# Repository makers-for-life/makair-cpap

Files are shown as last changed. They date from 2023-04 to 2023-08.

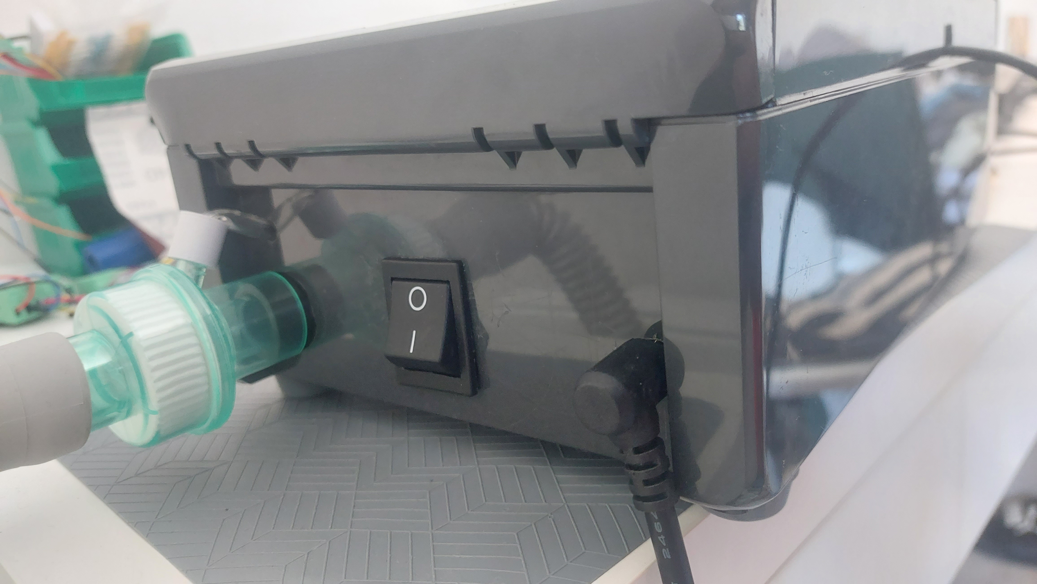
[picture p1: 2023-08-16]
Parts-CPAP/Case_V2/Output.jpg

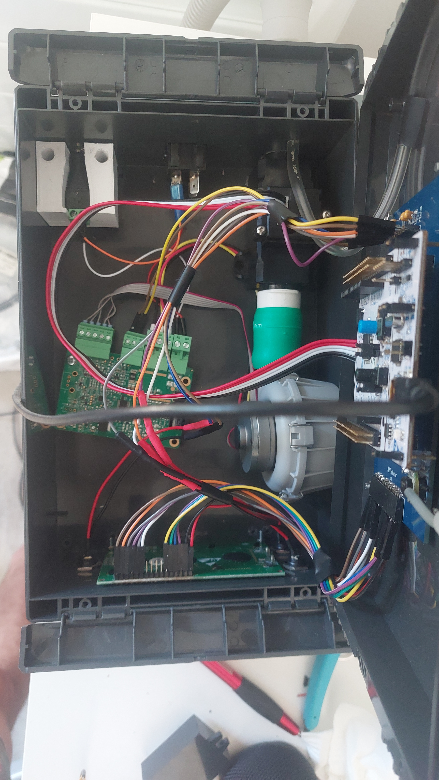
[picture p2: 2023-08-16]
Parts-CPAP/Case_V2/Input.jpg

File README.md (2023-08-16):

# MakAir CPAP

**Continuous Positive Airway Pressure ventilator for sleep apnea. Variant of the MakAir general-purpose ventilator.**

## Conception

This file lists all the documents that concern the design of the CPAP ventilator and the justification of all the choices that have been made on the system

[Conception-CPAP](https://github.com/makers-for-life/makair-cpap/tree/master/Conception-CPAP)

## Educational videos

This file lists the series of instructional videos on the progress of the CPAP ventilator project. You can find all the chapters of the project with educational files

[Educational videos](https://github.com/makers-for-life/makair-cpap/tree/master/Educational-videos)

## Firmware 

This file lists all the programs (Arduino, C++) that has been realized during the project. You can find the main program of the CPAP respirator which integrates the different operating modes

[Firmware-CPAP](https://github.com/makers-for-life/makair-cpap/tree/master/Firmware-CPAP)

## Motherboard 

This file lists all documents concerning the design and production of the PCB (BOM, Gerber, etc.).

[Motherboard-CPAP](https://github.com/makers-for-life/makair-cpap/tree/master/Firmware-CPAP)

## Parts

This file lists all files related to the mechanics of the CPAP ventilator. You can find the different parts in STL file and FreeCAD files

[Parts-CPAP](https://github.com/makers-for-life/makair-cpap/tree/master/Parts-CPAP)

## Various

This file lists various files that relate to specific information about the PPC ventilator

[Various-CPAP](https://github.com/makers-for-life/makair-cpap/tree/master/Various-CPAP)

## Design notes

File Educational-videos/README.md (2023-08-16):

| Chapter  | Content | Video  | File |
| ------------- | ------------- | ------------- | ------------- |
| 0  | **Introduction**  | [Introduction](https://www.youtube.com/watch?v=J2UsDe6RBvU&ab_channel=MakAir-Projetopensource) |  |
| 1  | This chapter will explain how to format a customer's need by structuring it with Sysml diagrams.  | [Chapter 1](https://www.youtube.com/watch?v=lZZDJNnGtbw&ab_channel=MakAir-Projetopensource)  | [Terms of reference](https://github.com/makers-for-life/makair-cpap/tree/master/Conception-CPAP)   |
| 2  | This chapter will explain the MCSE approach and how to use it to define the different I/O and system functions. |[Chapter 2](https://www.youtube.com/watch?v=BaCOPvmWCng&t=80s&ab_channel=MakAir-Projetopensource) | [MCSE](https://github.com/makers-for-life/makair-cpap/tree/master/Conception-CPAP)  |
| 3  | This chapter will explain how to choose the right components for each functional block defined above. Explain some important parameters to consider when choosing components. | [Chapter 3](https://www.youtube.com/watch?v=_1S2HhT8ymI&t=1s&ab_channel=MakAir-Projetopensource) | [Technological Choice](https://github.com/makers-for-life/makair-cpap/tree/master/Conception-CPAP)  |
| 4  | This chapter will explain why it is absolutely necessary to read the component datasheets and how this will allow us to have an electronic base of the system (definition of the pins for each component + realization of the electronic circuits).  | [Chapter 4](https://www.youtube.com/watch?v=aWXtmY03doI&ab_channel=MakAir-Projetopensource) | [Schematic](https://github.com/makers-for-life/makair-cpap/blob/master/Various-CPAP/Circuit_prototypage.png) |
| 5  | This chapter will explain how to define unit tests for each component to validate their operation against the requirements of the specifications.  | [Chapter 5](https://www.youtube.com/watch?v=EbR67JvbmO0&ab_channel=MakAir-Projetopensource) |[Unit tests](https://github.com/makers-for-life/makair-cpap/blob/master/Conception-CPAP/Tests_PPC.pdf)  |
| 6  | This chapter will explain what an IDE is, the different steps between the Arduino code and the binary file for the microcontroller and how to configure a compiler. | [Chapter 6](https://drive.google.com/file/d/1q3lwLBPiozaliIyiF1mZfMr3rwGGGQcm/view?usp=sharing)  | [Tuto STM32duino](https://github.com/makers-for-life/makair-cpap/blob/master/Educational-videos/Educational-sheets/Tuto_stm32duino.pdf)  |
| 7  | This chapter will explain how the blower works, the programming to make it work and the unit tests of the component. | [Chapter 7](https://www.youtube.com/watch?v=EbR67JvbmO0&ab_channel=MakAir-Projetopensource) | [Blower](https://github.com/makers-for-life/makair-cpap/blob/master/Educational-videos/Educational-sheets/Ptech_Blower.pdf)  |
| 8  | This chapter will explain how the flow meter works, the programming to make it work and the unit tests of the component.  |  [Chapter 8](https://drive.google.com/file/d/1uNUySGZBNgJsLLCi5F49UqdtfRMHSRPB/view?usp=sharing) | [Flow meter](https://github.com/makers-for-life/makair-cpap/blob/master/Educational-videos/Educational-sheets/Ptech_debitmetre.pdf)  |
| 9  | This chapter will explain how the pressure sensor works, the programming to make it work and the unit tests of the component. |  [Chapter 8](https://drive.google.com/file/d/1uNUySGZBNgJsLLCi5F49UqdtfRMHSRPB/view?usp=sharing) | [Pressure Sensor](https://github.com/makers-for-life/makair-cpap/blob/master/Educational-videos/Educational-sheets/Ptech_capteur_pression.pdf)  |
| 10  | This chapter will explain how to set up an HMI.  |  [Chapter 9](https://drive.google.com/file/d/1seV6_qKShw0mvWmM2Q1Elv6sRm0VnmUq/view?usp=sharing) | [HMI](https://github.com/makers-for-life/makair-cpap/blob/master/Educational-videos/Educational-sheets/Ptech_IHM.pdf) |
| 11  | This chapter will explain the integration (electronics and software) of each component seen previously to realize the prototype of the PPC ventilator. | [Chapter 10](https://drive.google.com/file/d/1VzoYUgVaH1z69m--aW6JiqTvfR3ldkRQ/view?usp=sharing) | [Integration](https://github.com/makers-for-life/makair-cpap/blob/master/Educational-videos/Educational-sheets/Ptech_Integration.pdf) |
| 12  | This chapter will explain the different parts to model and print in order to have a more presentable and usable prototype during its operation. | [Chapter 11](https://drive.google.com/file/d/1v5jeXeAJxhkbmkdimZctG2w2wa8iBlUA/view?usp=sharing)  | [Parts](https://github.com/makers-for-life/makair-cpap/tree/master/Parts-CPAP) |
| 13  | This chapter will explain how to model each 3D part in FreeCAD.  | [Chapter 11](https://drive.google.com/file/d/1v5jeXeAJxhkbmkdimZctG2w2wa8iBlUA/view?usp=sharing) | [CAD](https://github.com/makers-for-life/makair-cpap/blob/master/Educational-videos/Educational-sheets/Maquette_3D.pdf) |
| 14  | This chapter will explain the parameters to configure when printing the part modeled with Ultimaker Cura. | [Chapter 12](https://drive.google.com/file/d/1JHjJFGdZ1aSK9p1exW7JsYgn3sB551wM/view?usp=sharing) |  [3D printing](https://github.com/makers-for-life/makair-cpap/blob/master/Educational-videos/Educational-sheets/Maquette_3D.pdf) |
| 15  | This chapter will explain how to program a simple PPC mode in order to have a system that meets the specifications. |  [Chapter 13](https://drive.google.com/file/d/1Ri6_7VYuK2wYm5BPET0OP5y3Fja_Plpz/view?usp=sharing) | [Firmware](https://github.com/makers-for-life/makair-cpap/tree/master/Firmware-CPAP) [/ PPC Mode](https://github.com/makers-for-life/makair-cpap/blob/master/Educational-videos/Educational-sheets/Respirateur_PPC.pdf)  |
| 16  | **Conclusion** | [Chapter 14](https://drive.google.com/file/d/1DnsZAroqMhL1uKgiich44XQaq05BFfQ1/view?usp=sharing) |  |

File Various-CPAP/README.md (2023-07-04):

## Caractéristiques 

This document contains all the characteristic curves of the CPAP ventilator

## Nomenclature

This document lists all the components and references that make up the CPAP ventilator

## Circuit Prototypage

This document is a schematic diagram of the system circuit.

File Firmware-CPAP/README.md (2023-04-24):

## Arduino Code

This file contains all the Arduino codes for the prototyping of the system

## Firmware

| Component  | Includes | Sources  | Main |
| ------------- | ------------- | ------------- | ------------- |
| Blower  | [.h](https://github.com/makers-for-life/makair-cpap/blob/master/Firmware-CPAP/Includes/blower.h)  | [.cpp](https://github.com/makers-for-life/makair-cpap/blob/master/Firmware-CPAP/Sources/blower.cpp) | [.ino](https://github.com/makers-for-life/makair-cpap/blob/master/Firmware-CPAP/Main/Blower_fichier.ino) |
| AirFlow meter  | [.h](https://github.com/makers-for-life/makair-cpap/blob/master/Firmware-CPAP/Includes/airflowSensor.h)  | [.cpp](https://github.com/makers-for-life/makair-cpap/blob/master/Firmware-CPAP/Sources/airflowSensor.cpp) | [.ino](https://github.com/makers-for-life/makair-cpap/blob/master/Firmware-CPAP/Main/Debitmetre_fichier.ino) |
| Pressure Sensor  | [.h](https://github.com/makers-for-life/makair-cpap/blob/master/Firmware-CPAP/Includes/pressureSensor.h)  | [.cpp](https://github.com/makers-for-life/makair-cpap/blob/master/Firmware-CPAP/Sources/pressureSensor.cpp) | [.ino](https://github.com/makers-for-life/makair-cpap/blob/master/Firmware-CPAP/Main/Pressure_Sensor_fichier.ino) |
| HMI  | [.h](https://github.com/makers-for-life/makair-cpap/blob/master/Firmware-CPAP/Includes/IHM.h)  | [.cpp](https://github.com/makers-for-life/makair-cpap/blob/master/Firmware-CPAP/Sources/IHM.cpp) | |
| PPC  | [.h](https://github.com/makers-for-life/makair-cpap/blob/master/Firmware-CPAP/Includes/PPC.h)  | [.cpp](https://github.com/makers-for-life/makair-cpap/blob/master/Firmware-CPAP/Sources/PPC.cpp) | [.ino](https://github.com/makers-for-life/makair-cpap/blob/master/Firmware-CPAP/Main/Respirateur_PPC.ino) |

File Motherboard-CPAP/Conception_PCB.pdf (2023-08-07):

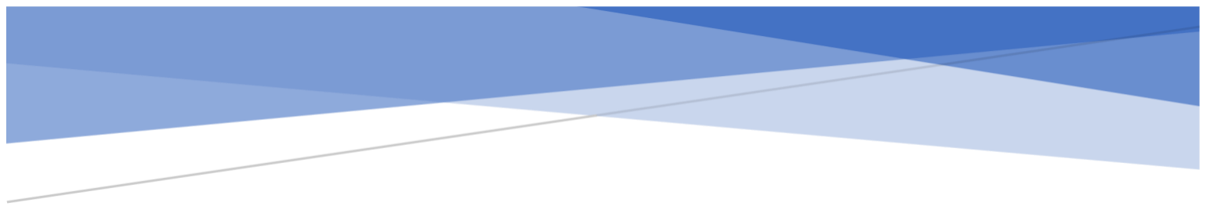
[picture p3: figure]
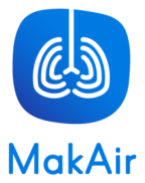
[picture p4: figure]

## BOUTRY Loan

### Alternant sur le projet MakAir

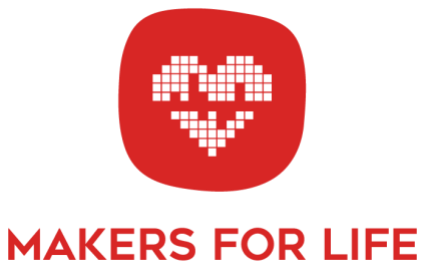
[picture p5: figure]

# PCB du Respirateur PPC

Ce document fait partie d’une série de livrables concernant la conception et le prototypage d’un respirateur à pression positive continue pour diminuer l’apnée du sommeil d’un patient

Ce livrable a pour but d’expliquer le développement du PCB du respirateur PPC afin de rendre le système plus fiable et moins encombrant. Nous pouvons retrouver toutes les solutions et composants choisies à mettre en place sur le PCB.

## Table des matières

Table des figures | 2
Comment concevoir un PCB ? | 3
Réalisation du schéma électronique | 3
Recherche des composants | 4
Routage de la carte | 5
Validation de la carte | 5
Présentation de la carte | 6
Schéma électronique | 6
Routage de la carte | 7
Validation de la carte | 8
Annexe | 10
BOM de la carte | 10

## Table des figures

Figure 1 : Schéma du capteur de pression | 3
Figure 2 : Recherche de composant | 4
Figure 3 : Schématique de la carte | 6
Figure 4 : TopLayer du PCB | 7
Figure 5 : BottomLayer du PCB | 7
Figure 6 : Photos du PCB (non assemblé et assemblé) | 8

## Comment concevoir un PCB ?

La conception d’une carte électronique se fait en 4 étapes :
- Réalisation du schéma électronique
- Recherche des composants
- Routage de la carte
- Validation de la carte.

Nous allons utiliser le logiciel EasyEDA pour concevoir notre carte, c’est un logiciel gratuit de conception de carte développé par JLCPCB (fabricant de PCB).

### Réalisation du schéma électronique

La première étape de la conception d’une carte est la réalisation d’une carte électronique afin de créer la base électronique de votre PCB. C’est dans cette étape qu’on relie les signaux de contrôle et d’alimentation entre le microcontrôleur et les différents composants. On va aussi mettre en place des fonctions électroniques (filtrage, amplification, …), améliorer la protection CEM (comptabilité électromagnétique) ou encore mettre des composants indispensables (capacité de découplage, LDO, …).

Pour imager l’étape, nous allons réaliser le câblage du capteur de pression :

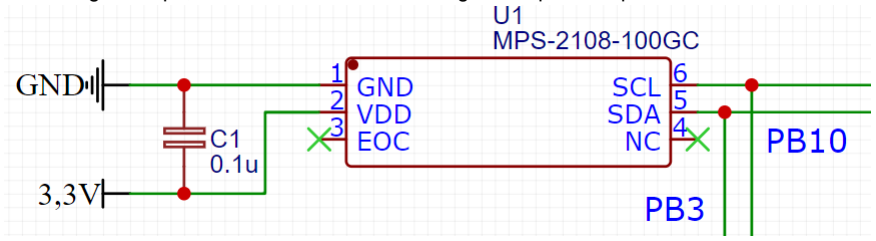
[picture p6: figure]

Figure 1 : Schéma du capteur de pression

Pour les signaux d’alimentation GND et VDD, on place des supply flags comme ci-dessous :

Ensuite on définit le VCC à 3,3V pour correspondre à l’alimentation du microcontrôleur. Pour le signal EOC et NC, on place un « Not Connect Flag » :

Enfin on relie la pin PB10 (broche 14 de U8) à SCL et PB3 (broche 8 de U8) à SDA qui correspondent à des broches de communication I2C du microcontrôleur :

Pour finaliser le câblage du capteur de pression, il faut placer une capacité (0,1µF) de découplage entre VDD et GND et placer des résistances en parallèle des signaux SCL et SDA comme ci-dessous :

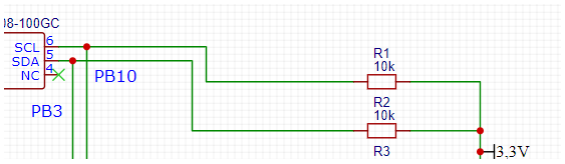
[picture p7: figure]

Le câblage du capteur de pression est réalisé. Il est important d’être rigoureux sur cette étape, on peut utiliser des logiciels comme LTSpice pour simuler le câblage et valider au préalable le schéma électronique.

### Recherche des composants

Cette étape consiste à choisir les composants du schéma électronique. Pour les résistances et condensateurs nous allons choisir entre des composants traversants ou CMS. Pour les connecteurs, nous allons choisir le pas entre chaque trou (pour notre cas, nous allons choisir que des pas de 2,54 mm). Pour le capteur de pression, on va choisir la référence de notre capteur de pression. Cette étape va permettre d’avoir les empreintes de chaque composant pour le routage de la carte. Avec EasyEDA, cette étape est automatiquement faite quand on place les composants sur le schéma mais il peut arriver sur des logiciels (ex : Kicad) qu’on doit rechercher ou créer des empreintes. Pour bien choisir les empreintes des composants sur EasyEDA, on doit aller sur « Library » rechercher la référence du composant (ex : pressure sensor MPS) et le placer sur le schéma :

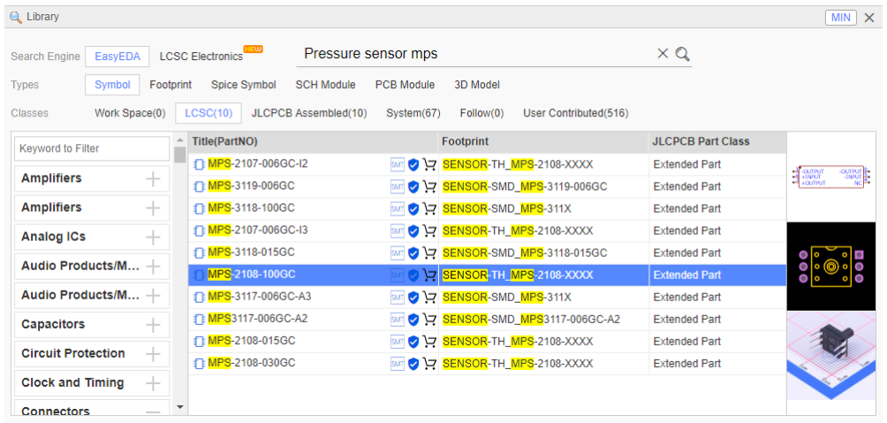
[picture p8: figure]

Figure 2 : Recherche de composant

Dès que on a placé tous les composants, on génére le BOM (Bill of materials) pour récupérer tous les détails des composants sur un tableur. Le BOM de la carte électronique du respirateur PPC est en Annexe.

### Routage de la carte

Cette étape consiste à positionner les composants et relier les signaux avec des pistes. C’est en quelque sorte la construction de la carte. Cela va définir beaucoup de paramètres : le dimensionnement de la carte, le nombre de couches au PCB, la largeur des pistes et le nombre de vias (connexion entre 2 couches). C’est aussi la partie la plus « créative » de la conception puisque on a énormément de possibilités pour router la carte (si on a des contraintes, les possibilités vont forcément diminuer). Au vu du nombre de possibilités pour le routage de la carte, il est important de connaître des règles indispensables :

- La largeur des pistes : Plus la tension parcourant la piste est haute, plus la largeur de votre piste est grande. Dans notre cas, les signaux d’alimentation sont à 1 mm et les signaux de contrôle sont à 0,254 mm.
- Le diamètre des trous/vias (composant traversant) : le diamètre de l’empreinte (zone servant à souder les composants) doit être 2 fois plus grande que le trou
- Aucun angle droit sur les pistes : il est important de ne pas avoir d’angle à 90° sur les pistes afin de les renforcer dans la durée
- La piste doit toujours arriver droite sur l’empreinte :
- Plan de masse : Un plan de masse est une zone reliant toutes les broches GND en commun. Cela permet d’avoir qu’une seule masse en commun pour tous les composants pour éviter des problèmes sur l’alimentation de votre carte. Pour notre cas on la met sur la partie composant (Top) de notre carte :

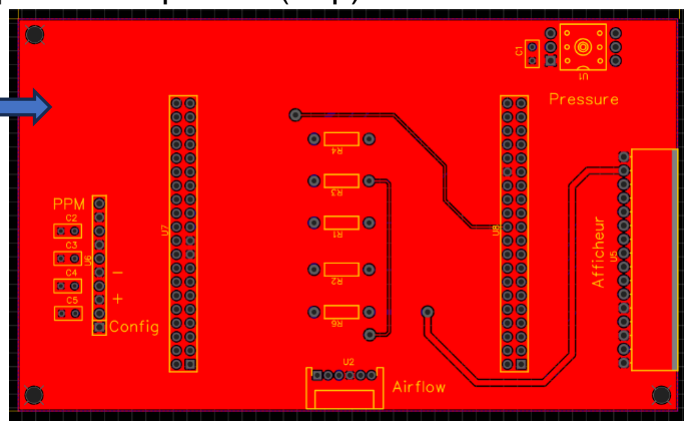
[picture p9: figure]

- Placer des vias si on n’a pas le choix : il est important d’avoir le moins de vias possibles sur votre carte
- Placer la capacité de découplage au plus près du composant :

### Validation de la carte

Cette dernière étape concerne les tests unitaires pour chaque composant afin de valider le fonctionnement de la carte. Pour cette étape il est important d’assembler au fur à mesure la carte pour tester une fonction seule pour retrouver plus facilement le problème s’il y en a un. Dès qu’on a testé unitairement chaque composant, on réalise un test d’intégration pour tester la carte dans sa globalité. Pour avoir une meilleure visibilité sur les tests, on met les résultats de chaque test dans un tableur.

Plan de
masse

## Présentation de la carte

Le but du PCB est de développer une carte permettant d’enlever les fils du prototypage et de placer chaque composant du système sur la carte. Cela va permettre de rendre le système plus fiable et moins encombrant au niveau électronique. Le PCB est une première version de prototypage, c’est pour cela que l’on utilise seulement des connecteurs pour placer les composants (microcontrôleur, débitmètre, capteur de pression et IHM).

### Schéma électronique

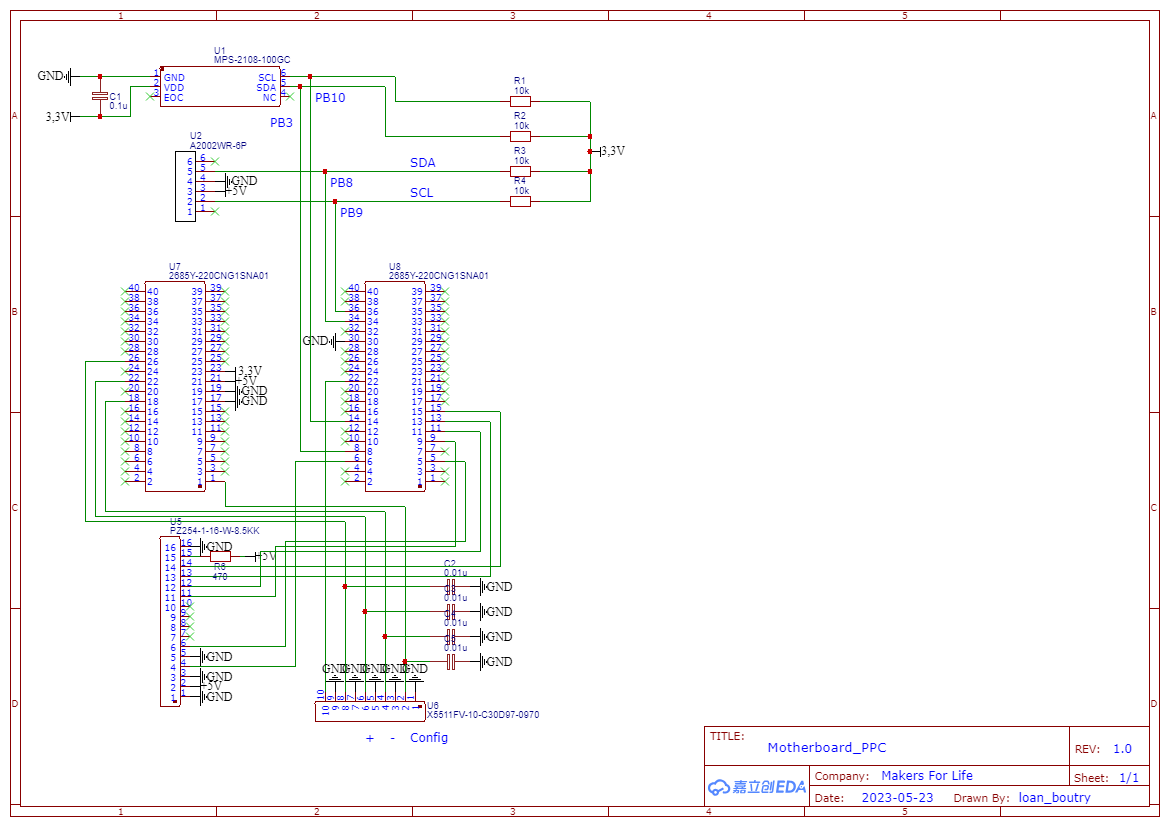
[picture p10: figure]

Figure 3 : Schématique de la carte

Nom | Rôle | Remarques
U1 | Emplacement du capteur de pression | Reference : ABP2MRRT060MD2A3XX
U2 | Connecteur du débitmètre | Reference : Honeywell Zephyr
U5 | Connecteur de l’afficheur LCD (Communication en série) | Reference : Displaytech 204A
U6 | Connecteur des boutons poussoirs | Câblage en Pull-Up
U7/U8 | 2 connecteurs pour la Nucleo STM32F411RE
R1..4 | Résistances 10k pour les 2 communications I2C
R5 | Résistance 470Ω pour la luminosité de l’afficheur
C1 | Capacité de découplage de 0,1µF pour le capteur de pression
C2..C5 | Capacités de 0,01µF pour une protection CEM
H1..H4 | Connecteurs pour les boutons poussoirs de l’IHM | 3 boutons sont utilisés (+, - et config). Un 4ème est ajouté si besoin
H5 | Connecteur du blower pour le signal PPM

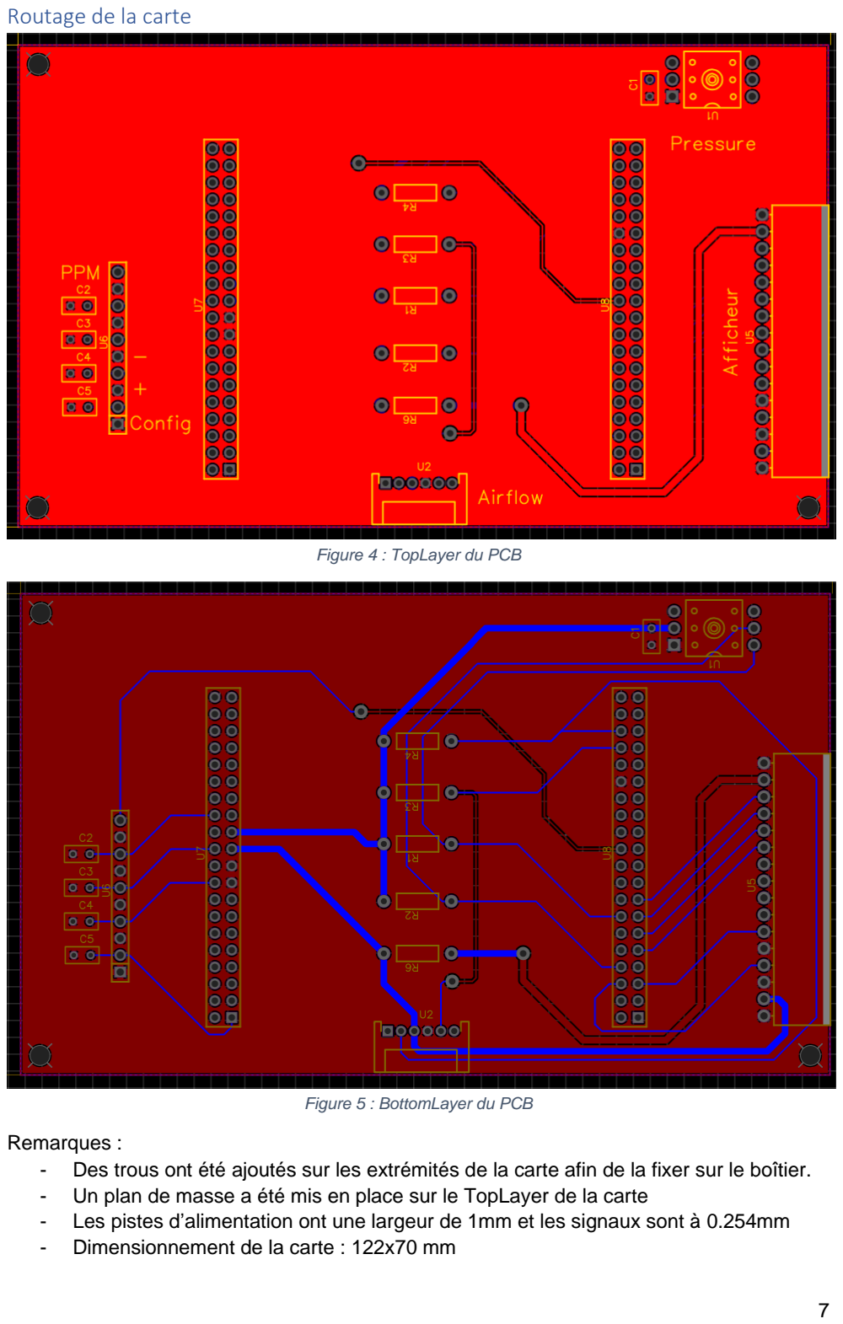
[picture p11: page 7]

### Routage de la carte

Figure 4 : TopLayer du PCB

Figure 5 : BottomLayer du PCB

Remarques :
- Des trous ont été ajoutés sur les extrémités de la carte afin de la fixer sur le boîtier.
- Un plan de masse a été mis en place sur le TopLayer de la carte
- Les pistes d’alimentation ont une largeur de 1mm et les signaux sont à 0.254mm
- Dimensionnement de la carte : 122x70 mm

### Validation de la carte

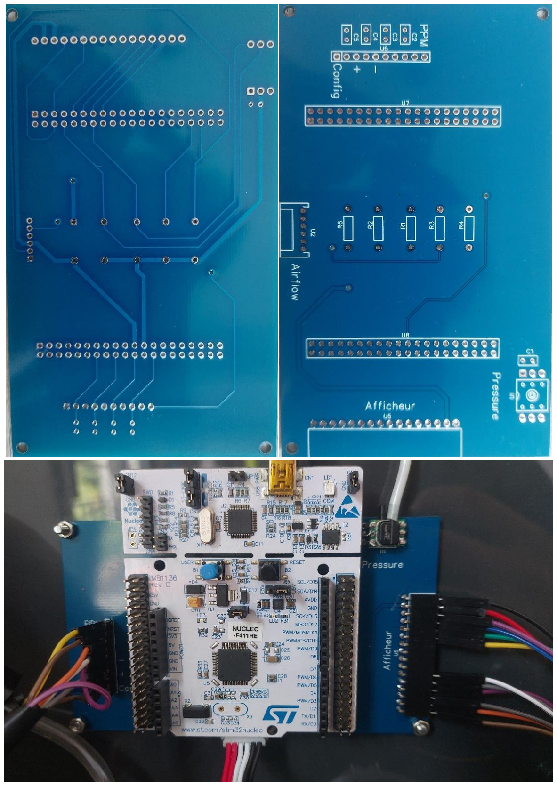
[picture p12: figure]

Figure 6 : Photos du PCB (non assemblé et assemblé)

Nous allons vérifier les alimentations s’il n’y a aucun problème (court-circuit, baisse de tension) et si les signaux de contrôle correspondent au programme intégré dans le microcontrôleur. S’il y a des modifications à réaliser, nous referons une deuxième version de la carte.

V1 :

Elément testé sur le PCB | Validation ? | Remarques
Alimentation | OUI | - Conversion du 24V au 5V est fonctionnel pour le µC - Carte de contrôle alimentée en 24V
Blower | OUI | - Pas besoin de souder le via - Penser à souder le GND du µc au PCB
Débitmètre | OUI | - Faire attention à ne pas confondre le 3,3V et le 5V - Câbler les 5 résistances pour faire fonctionner le capteur
Capteur de pression | NON | - Refaire le positionnement du capteur de pression (validé si l’on change de sens) - Faire attention au sens du capteur lors de la soudure
IHM | NON | - Problème d’alimentation sur la Pin d’alimentation de l’afficheur - Config non fonctionnel à cause d’une broche non adaptée à la fonction

V2 :

Elément testé sur le PCB | Validation ? | Remarques
Alimentation | OUI
Blower | OUI
Débitmètre | OUI
Capteur de pression | OUI | - Capteur de pression dans le bon sens -Récupération des données fonctionnelle
IHM | OUI | - Affichage des données fonctionnel -Configuration des paramètres fonctionnelle

## Annexe

### BOM de la carte

ID | Name | Designator | Footprint | Quantity | Manufacturer | Supplier | Pins
1 | 0.1u | C1 | RAD-0.1 | 1 | | | 2
2 | 0.01u | C2,C3,C4,C5 | RAD-0.1 | 4 | | | 2
3 | 10k | R1,R2,R3,R4 | R_AXIAL-0.4 | 4 | | | 2
4 | 470 | R6 | R_AXIAL-0.4 | 1 | | | 2
5 | MPS-2108-100GC | U1 | SENSOR-TH_MPS-2108-XXXX | 1 | 全磊 | LCSC | 6
6 | A2002WR-6P | U2 | CONN-TH_6P-P2.00_C273067 | 1 | Changjiang Connectors | LCSC | 6
7 | PZ254-1-16-W-8.5KK | U5 | HDR-TH_16P-P2.54-H-F-W10.0-N | 1 | HCTL(华灿天禄) | LCSC | 16
8 | X5511FV-10-C30D97-0970 | U6 | HDR-TH_10P-P2.54-V-F | 1 | XKB Connectivity(中国星 坤) | LCSC | 10
9 | 2685Y-220CNG1SNA01 | U7,U8 | HDR-TH_40P-P2.54-V-F-R2-C20-S2.54 | 2 | 华宇创 | LCSC | 40

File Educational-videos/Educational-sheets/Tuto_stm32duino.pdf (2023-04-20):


## BOUTRY Loan

### Alternant sur le projet MakAir


# Installation de l’environnement stm32duino

Ce document fait partie d’une série de livrables concernant la conception et le prototypage d’un respirateur à pression positive continue pour diminuer l’apnée du sommeil d’un patient

Ce livrable a pour but d’expliquer les étapes pour installer l’environnement de travail. Celuici est basé sur le microcontrôleur STM32F411RE et Arduino IDE. Pour suivre les étapes, il faut avoir installé Arduino IDE

## Table des matières

Table des figures | 2
C’est quoi stm32duino ? | 2
https://github.com/stm32duino | 2
Etapes d’installation | 3
Etape 1 : Installer stm32duino | 3
Etape 2 : Configurer le compilateur | 4
Etape 3 : Compiler et téléverser vers la cible | 5
Etape bonus : Installer des librairies | 7

## Table des figures

Figure 1 : Additional Boards Manager | 3
Figure 2 : Installation de STM32 MCU based boards | 3
Figure 3 : Sélection des boards | 4
Figure 4 : Sélection de la board générique | 4
Figure 5 : Sélection de la référence | 5
Figure 6 : Chemin de la compilation | 5
Figure 7 : Fichier .bin | 6
Figure 8 : Téléversement du programme | 6
Figure 9 : Serial.print un Hello World | 7
Figure 10 : Gérer les librairies | 7
Figure 11 : Installation d'une librairie | 7

## C’est quoi stm32duino ?

C’est un environnement créé par la communauté Arduino qui contient différents cœurs de la gamme STM32. Chaque cœur a été développé pour que le compilateur d’Arduino IDE puisse être compatible avec la cible STM32 afin que tous les périphériques et fonctionnalités que propose d’un cœur puisse être pris en compte lors de la compilation du programme. La mise en place de cet environnement est obligatoire. L’avantage de stm32duino est que l’on peut utiliser certaines librairies d’un cœur Arduino (plus simple d’utilisation) sur un cœur STM32. Dans notre cas, ce qui nous intéresse est la gamme STM32F4 series et particulièrement le cœur du STM32F411RE

Cet environnement est retrouvable sur le github ci-dessous :

https://github.com/stm32duino

## Etapes d’installation

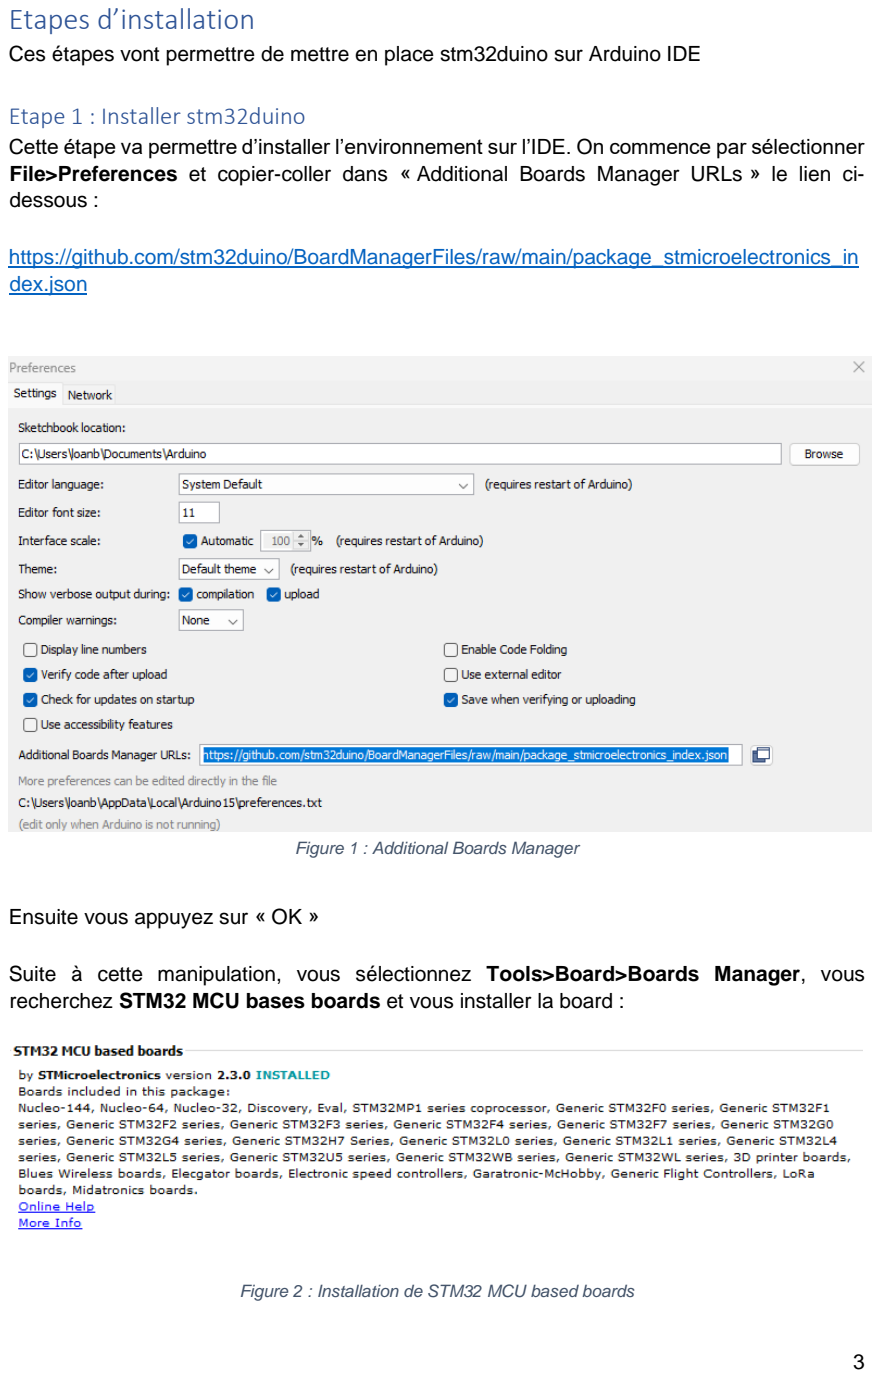
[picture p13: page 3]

Ces étapes vont permettre de mettre en place stm32duino sur Arduino IDE

### Etape 1 : Installer stm32duino

Cette étape va permettre d’installer l’environnement sur l’IDE. On commence par sélectionner File>Preferences et copier-coller dans « Additional Boards Manager URLs » le lien ci-dessous :

https://github.com/stm32duino/BoardManagerFiles/raw/main/package_stmicroelectronics_in dex.json (https://github.com/stm32duino/BoardManagerFiles/raw/main/package_stmicroelectronics_index.json)

Figure 1 : Additional Boards Manager

Ensuite vous appuyez sur « OK »

Suite à cette manipulation, vous sélectionnez Tools>Board>Boards Manager, vous recherchez STM32 MCU bases boards et vous installer la board :

Figure 2 : Installation de STM32 MCU based boards

Lorsque l’installation est finie, vous fermez la fenêtre et vous pouvez sélectionnez Tools>Board et normalement vous avez 2 boards qui s’affichent :


Figure 3 : Sélection des boards

Si vous avez « STM32 boards group » vous avez donc réussi à installer stm32duino sur votre IDE. Maintenant il faut configurer le compilateur afin de sélectionner le cœur STM32 correspondant à la cible et les différents paramètres de compilation.

### Etape 2 : Configurer le compilateur

Tout d’abord, il faut sélectionner le cœur STM32F411RE. Pour cela il faut sélectionner Tools>Board>STM32 boards group>Generic STM32F4 series :

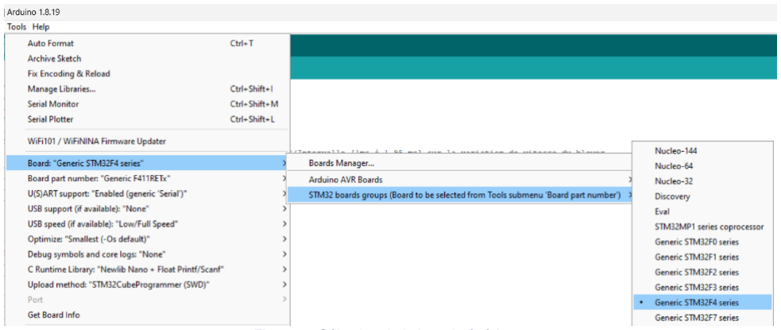
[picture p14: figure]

Figure 4 : Sélection de la board générique

Ensuite, choisissez la bonne référence Tools>Board part number>Generic F411RETx :

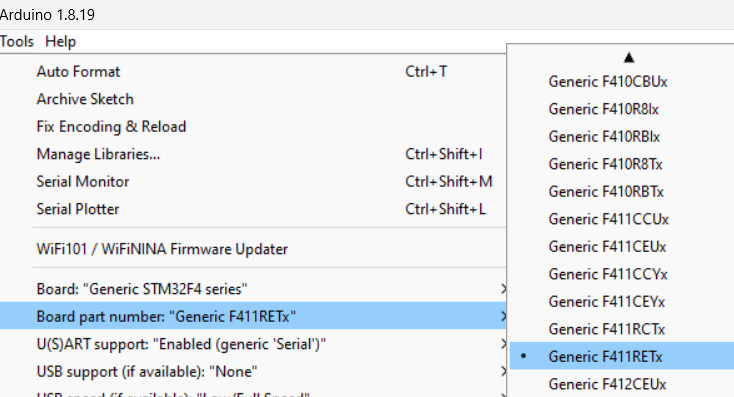
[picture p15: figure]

Figure 5 : Sélection de la référence

Vous avez maintenant un compilateur compatible avec votre cible STM32F411RE, vous pouvez configurer certains paramètres de la compilation pour l’optimiser :
- U(S)ART support : C’est un paramètre qui permet de sélectionner la communication entre l’ordinateur et la cible. Si vous utilisez un port USB, laissez le paramètre par défaut « Enabled(generic « Serial ») »
- USB speed : C’est un paramètre qui permet de configurer la vitesse de la communication entre l’ordinateur et la cible
- Optimize : C’est un paramètre qui permet de sélectionner le mode d’optimisation lors de la compilation. Vous pouvez laisser le mode par défaut.
- Upload Method : C’est un paramètre qui permet de choisir le mode de téléversement du code. Ce paramètre ne nous intéresse pas puisque l’on va utiliser une autre méthode pour téléverser

Il nous reste plus qu’à compiler et téléverser le programme vers la cible

### Etape 3 : Compiler et téléverser vers la cible

Pour compiler le programme, il suffit d’appuyer sur ce bouton :

Vous attendez que le programme se compile et vous récupérez le chemin de compilation :

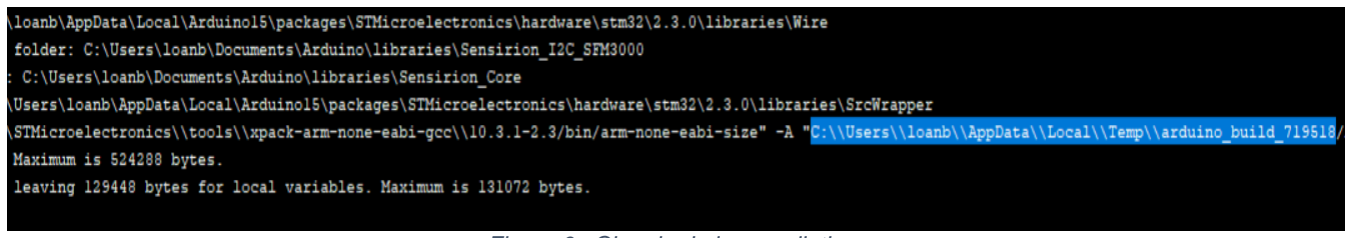
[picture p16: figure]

Figure 6 : Chemin de la compilation

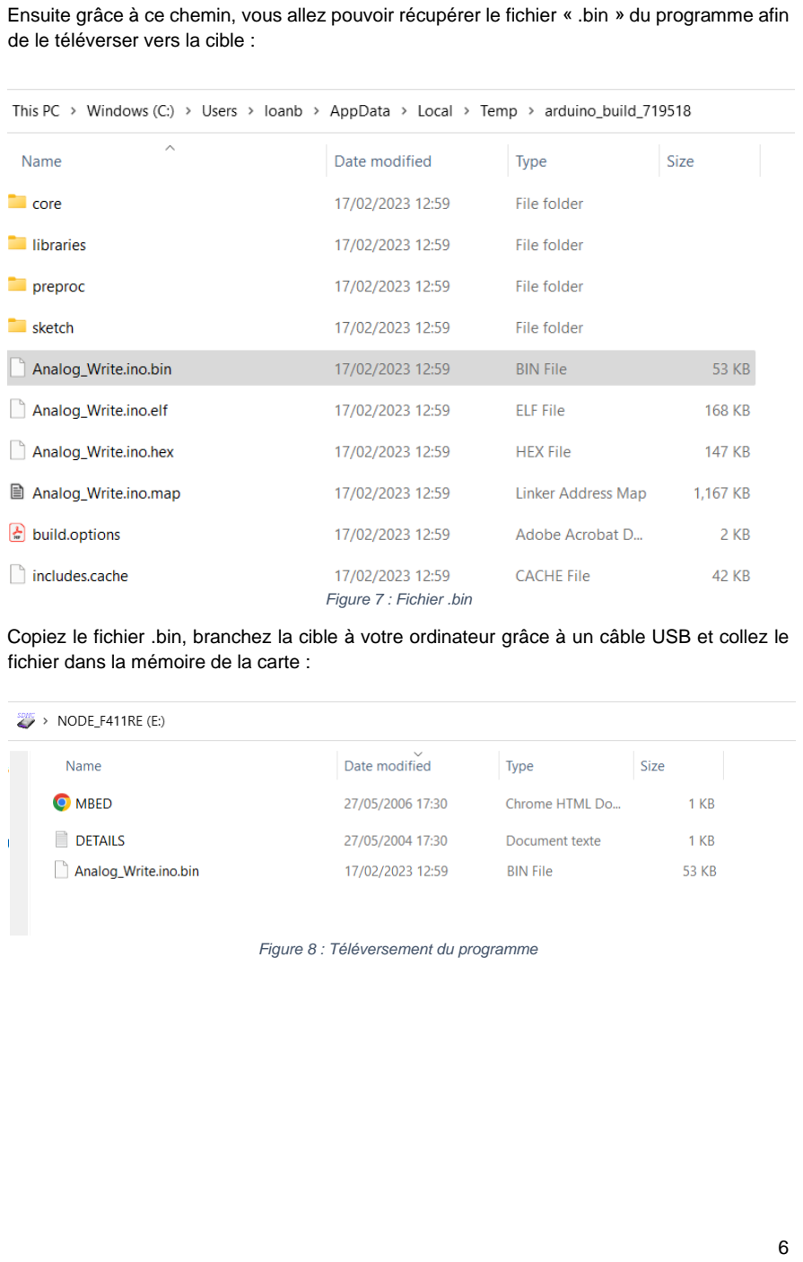
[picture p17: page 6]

Ensuite grâce à ce chemin, vous allez pouvoir récupérer le fichier « .bin » du programme afin de le téléverser vers la cible :

Figure 7 : Fichier .bin

Copiez le fichier .bin, branchez la cible à votre ordinateur grâce à un câble USB et collez le fichier dans la mémoire de la carte :

Figure 8 : Téléversement du programme

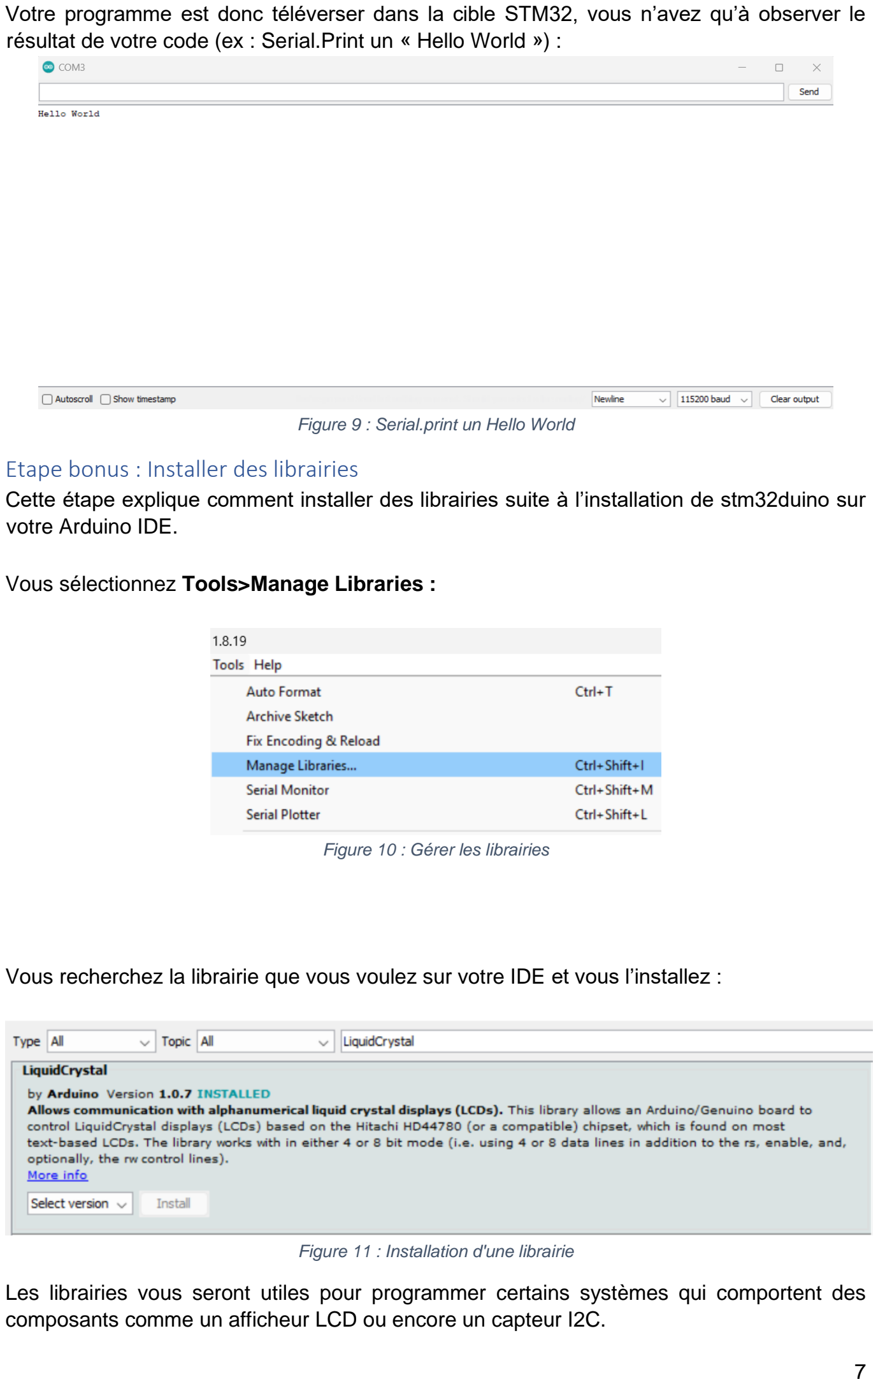
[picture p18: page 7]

Votre programme est donc téléverser dans la cible STM32, vous n’avez qu’à observer le résultat de votre code (ex : Serial.Print un « Hello World ») :

Figure 9 : Serial.print un Hello World

### Etape bonus : Installer des librairies

Cette étape explique comment installer des librairies suite à l’installation de stm32duino sur votre Arduino IDE.

Vous sélectionnez Tools>Manage Libraries :

Figure 10 : Gérer les librairies

Vous recherchez la librairie que vous voulez sur votre IDE et vous l’installez :

Figure 11 : Installation d'une librairie

Les librairies vous seront utiles pour programmer certains systèmes qui comportent des composants comme un afficheur LCD ou encore un capteur I2C.

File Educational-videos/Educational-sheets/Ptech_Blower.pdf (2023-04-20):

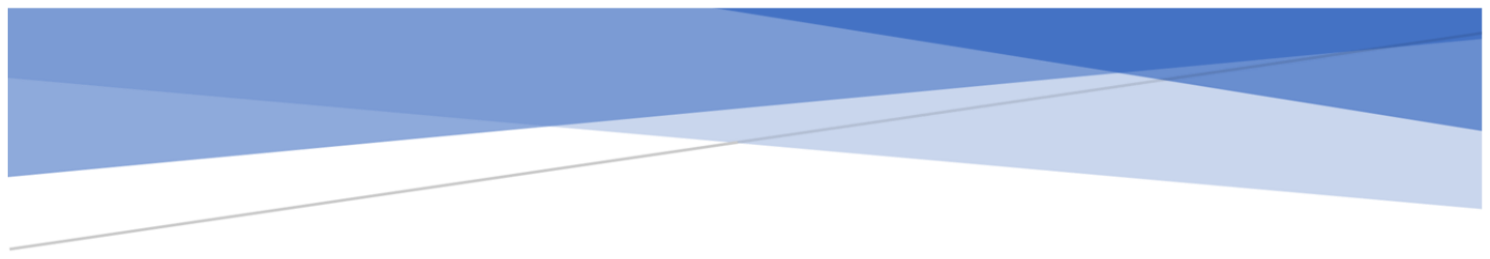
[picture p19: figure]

## BOUTRY Loan

### Alternant sur le projet MakAir


# Commande du Blower

Ce document fait partie d’une série de livrables concernant la conception et le prototypage d’un respirateur à pression positive continue pour diminuer l’apnée du sommeil d’un patient

Ce livrable a pour but d’expliquer le fonctionnement du blower intégré dans le MakAir. La première partie du document est une analyse des 4 éléments nécessaires pour activer le blower. La deuxième partie portera sur la génération d’une commande PPM et la dernière partie sera sur les résultats de la commande de la turbine.

## Table des matières

Table des figures | 2
Analyse du système | 3
Carte de puissance | 3
Carte de contrôle | 4
Blower | 5
Générateur du signal PPM | 6
Génération d’un signal PPM | 7
C’est quoi un signal PPM ? | 7
Fonction digitalWrite | 8
PWM avec un timer/counter | 8
Les différentes versions de la commande du Blower | 10
Commande simple | 10
Variation de la vitesse | 10
Annexe | 11
Annexe 1 : Librairie « hardwareTimer.h » | 11
Annexe 2 : Code de la commande simple | 12
Annexe 3 : Variation de la Vitesse | 12

## Table des figures

Figure 1 : SCP-75-12 | 3
Figure 2 : Schéma de la carte de contrôle | 4
Figure 3 : Blower du MakAir | 5
Figure 4 : Caractéristique du blower : pression et débit d'air | 5
Figure 5 : Schéma GPIO du STM32F411RE | 6
Figure 6 : Schéma complet de la commande du blower | 7
Figure 7 : Signal PPM | 7
Figure 8 : Code avec la fonction digitalWrite | 8
Figure 9 : Principe d'un Timer/Counter | 8
Figure 10 : Code de configuration du Timer/Counter | 9

## Analyse du système

Cette partie énumère les éléments nécessaires au fonctionnement du blower : la carte de puissance, la carte de contrôle, le blower et le générateur du signal PPM. Chaque élément comportera un schéma et des explications sur son rôle dans le système

### Carte de puissance

C’est l’élément permettant d’apporter la puissance nécessaire pour que le blower puisse fonctionner dans les conditions optimales. En général, c’est la carte qui va permettre de transformer la tension électrique alternative du secteur (220V ~ 50Hz) en une tension continue (12V dans notre cas). En plus d’apporter la puissance nécessaire à la turbine, nous pouvons coupler le système avec des batteries afin de le rendre autonome en cas d’urgence.

Si nous revenons à notre cas du blower intégré au MakAir, la fiche technique de la carte de contrôle nous indique qu’il peut supporter une tension de 11 à 25V (avec 12V en tension optimale) et tirer un courant continu jusqu’à 3A. Cela nous permet de savoir que l’on doit choisir une carte de puissance avec une sortie de 12 à 24V et ayant un courant ≤ 3A.

Dans notre système nous avons choisi un SCP-75-12 :

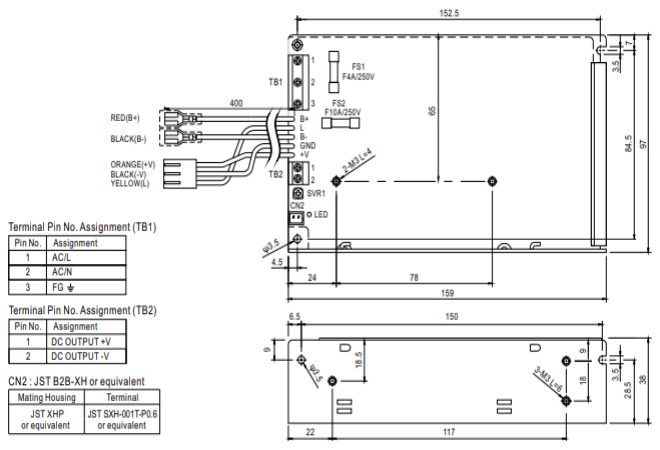
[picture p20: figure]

Figure 1 : SCP-75-12

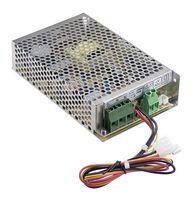
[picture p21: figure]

C’est une carte de puissance qui fournit :

Tension nominale | 13,8V
Plage de courant | 0 ~ 5,4A
Puissance nominale | 74,5W

Cette carte sera donc la partie puissance de notre commande du blower.

### Carte de contrôle

C’est l’élément qui va permettre de gérer la puissance à envoyer à la turbine et de contrôler le fonctionnement et le sens du blower grâce à 6 transistors MOSFET. Pour comprendre simplement le système : le blower est composé d’un moteur brushless. Celui-ci est un moteur sans balai c’est-à-dire qu’à la place des balais nous avons 3 bobines avec 2 transistors MOSFET par bobine. Ça permet de contrôler le sens du moteur en fonction des bobines actives et des transistors. Un élément peut se rajouter au moteur pour connaître le sens et la vitesse. Dans notre cas, c’est un capteur à effet hall intégré au moteur qui nous renvoie ces données à la carte.
La carte de contrôle va aussi réguler la vitesse du blower selon la consigne envoyée par un signal PPM depuis le microcontrôleur. Cette régulation met en oeuvre des asservissements complexes faisant intervenir le courant passant dans chaque phase (mesuré par des capteurs de courant), et de la position du moteur (mesurée par des capteurs à effet Hall). Elle est réalisée de façon autonome par la carte de contrôle et ne rentre pas dans le cadre de cette étude.

En général, le blower est fourni avec sa carte de contrôle puisqu’elle est compatible seulement avec celle-ci. C’est notre cas avec le blower intégré au MakAir :

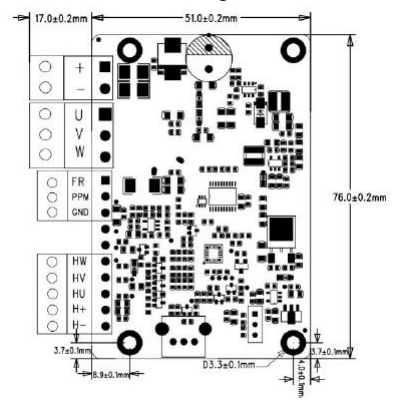
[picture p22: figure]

Figure 2 : Schéma de la carte de contrôle

+ - | Sortie + de la carte de puissance (SCP-75-12) Sortie – de la carte de puissance
U V W | 12 V pour l’entrée du blower (red) GND pour l’entrée du blower (black) Signal de contrôle du blower (yellow)
FR PPM GND | Signal PPM de 50Hz envoyé par le générateur GND du générateur de PPM
HW HV HU H+ H- 🡪GND | Signaux de contrôle du sens et de la vitesse du blower

Nous savons aussi que la variation de la vitesse de blower se fait entre 1,08 ms et 1,86 ms pour le « High Level Pulse » du signal PPM

### Blower

C’est l’élément central qui va nous permettre d’envoyer de l’air en pression positive continue. Celui-ci comporte un moteur brushless (sans balai) qui va aspirer l’air environnant pour l’envoyer sous un certain débit. C’est un composant généralement utilisé dans les aspirateurs, VMC ou encore dans les respirateurs médicaux.
Le blower intégré au MakAir est un cas un peu particulier puisque nous avons peu d’informations. Ce que l’on sait :
Plage de tension | 6 à 30V
Plage de courant | < 1,4A
Plage de vitesse | 0 à 33000 rpm
Pression en sortie | 1000 Pa

Ces informations nous permettent de déduire qu’il est plutôt adapté à notre système de respirateur PPC contre l’apnée du sommeil.

On peut aussi retrouver la connectique de la turbine ci-dessous :

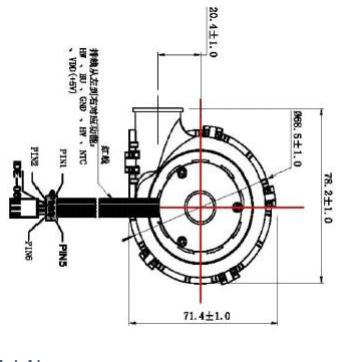
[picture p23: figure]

Figure 3 : Blower du MakAir

La caractéristique entre le débit d’air et la pression est donnée pour connaître les points extrêmes du blower (pression max et débit max). Nous pouvons la retrouver ci-dessous :

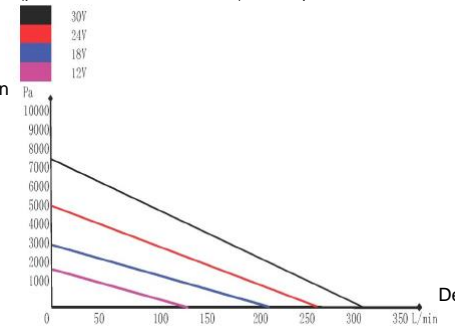
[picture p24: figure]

Figure 4 : Caractéristique du blower : pression et débit d'air

Débit

Pression

### Générateur du signal PPM

C’est l’élément essentiel pour gérer la vitesse de la turbine. Dans notre cas, le signal PPM va être généré par un microcontrôleur STM32F411RE. Une des sorties va générer un signal PPM avec des outils intégrés au microcontrôleur : par une sortie numérique ou par timer/counter générant un signal PWM.

Les caractéristiques du microcontrôleur STM32F411RE sont intéressantes car très performantes pour notre système :
- Processeur 32 bits
- Tension d’alimentation de 1,7 à 3,6V
- 512 Kbytes de mémoire Flash et 128 Kbytes de mémoire RAM
- 11 timers : six de 16 bits et deux de 32 bits avec chacun quatre channels Input Compare/Output Compare/PWM/Pulse counter. Ensuite deux watchdog timers et un SysTick timer
- Serial wire debug (SWD) pour le debug
- ADC de 12 bits avec 16 channels
- 81 I/O ports avec une capacité d’interruption
- 3 interfaces I²C, 3 interfaces USART et 5 interfaces SPI

Pour notre prototypage de la commande du blower, nous avons choisi le port PB6 (D10) pour générer le signal PPM. Le port comporte les fonctions ci-dessous :

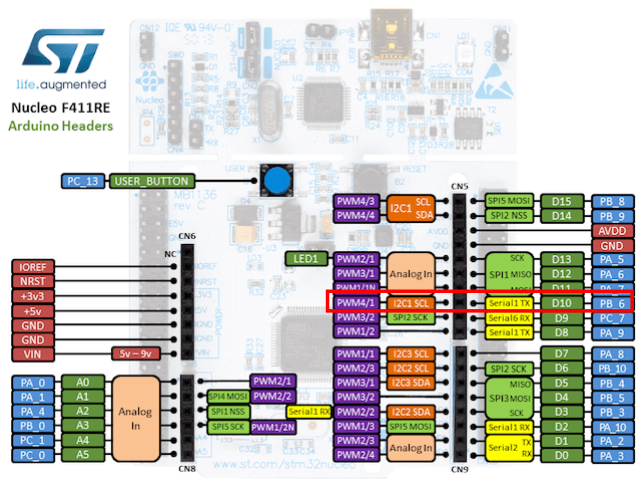
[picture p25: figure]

Figure 5 : Schéma GPIO du STM32F411RE

Il est très important de faire attention au timer/counter et au channel PWM correspondant au port choisi. Sur le port D10, nous sommes sur le TIM4 channel 1.

Si on assemble les 4 éléments de la commande du blower, on peut en déduire ce schéma :

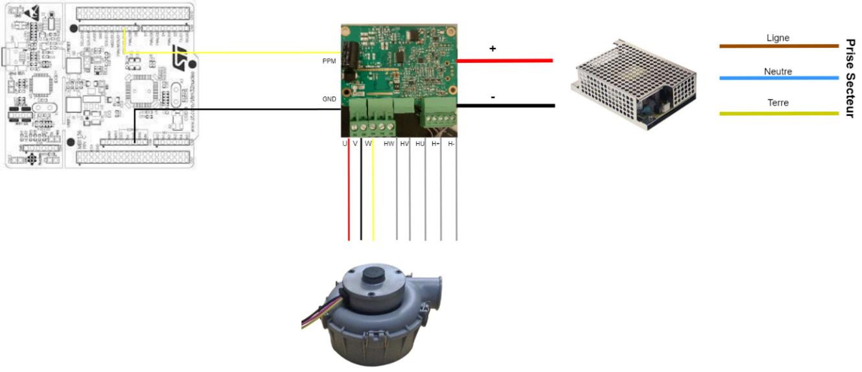
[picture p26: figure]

Figure 6 : Schéma complet de la commande du blower

Maintenant que nous avons présenté tous nos éléments, nous allons expliquer comment générer un signal PPM pour activer et contrôler la vitesse.

## Génération d’un signal PPM

Cette partie va introduire les fonctions nécessaires pour générer un signal PPM de 50 Hz sur le port PB6. Il y a 2 manières différentes : avec une fonction simple sur une sortie numérique et avec la génération d’une PWM avec un timer/counter.

### C’est quoi un signal PPM ?

Un signal PPM (Pulse-Position Modulation) est comparable a un signal PWM sauf qu’à la place d’utiliser un rapport cycle de 0 à 100%, on va varier le signal sur une intervalle de rapport cyclique beaucoup plus courte. Le signal PPM est dépendant d’un signal carré puisque celui-ci est sa référence en période.


Figure 7 : Signal PPM

C’est un signal souvent utilisé pour la modulation pour faire une liaison « point-à-point » entre un émetteur et récepteur par exemple entre une télécommande et un drone.

### Fonction digitalWrite

Une première approche pour générer notre signal PPM consiste à utiliser la fonction digitalWrite, en activant la sortie pendant un court instant.
Cette fonction est très simple à mettre en place mais le principal problème c’est que si nous ajoutons d’autres fonctions (débitmètre, afficheur LCD, …), cette fonction risque d’occuper le microcontrôleur tout le temps à cause des « delayMicroseconds ». Donc la fonction digitalWrite nous permet d’activer le blower et de réguler sa vitesse mais sans pouvoir ajouter d’autres fonctions importantes pour notre système.

#define PIN_ESC_BLOWER PB6 // D10

void setup() {

pinMode(PIN_ESC_BLOWER,OUTPUT);

void loop() {
digitalWrite(PIN_ESC_BLOWER, LOW);
Min = delayMicroseconds(1750); ou Max = delayMicroseconds(50); digitalWrite(PIN_ESC_BLOWER, HIGH);
Min = delayMicroseconds(250); ou Max = delayMicroseconds(1950); }

Figure 8 : Code avec la fonction digitalWrite

Précision sur la fonction AnalogWrite :
Le blower va pouvoir être activé mais ne va pas pouvoir être commandé en vitesse à cause de la fréquence PWM en sortie de la fonction AnalogWrite. La cause est dû à la précision de la génération du signal PPM de 50 Hz puisque la sortie numérique ne peut générer qu’une PWM de 1,1 kHz. Cela n’est pas suffisant pour avoir une précision de variation du « High Level Pulse » inférieure 1 ms (pour varier entre 1,08 et 1,86 ms).

Avec une sortie numérique qui génère une fréquence de 1,1 kHz, la précision de la variation du rapport cyclique est de 0,9 ms. Donc on peut en déduire que c’est trop grand pour faire varier le signal entre 1,08 et 1,86 ms.

### PWM avec un timer/counter

Cette fonction est plus complexe mais permet d’avoir une commande beaucoup plus précise sur la vitesse du blower. Nous allons utiliser un élément important d’un processeur, c’est le Timer/Counter qui permet généralement de déclencher une instruction/fonction lorsque le Timer a atteint le Flag que l’on a défini lors de la configuration.


Figure 9 : Principe d'un Timer/Counter

Les Timer/Counter ont généralement 4 modes d’utilisation : IC (Input Compare), OC (Output Compare), PWM et Pulse counter. C’est le mode PWM qui nous intéresse dans notre cas puisque celui-ci va générer un signal PWM en fonction de la configuration attribuée.

Pour utiliser le timer/counter sur le STM32F411RE, nous allons prendre la librairie « hardwareTimer » pour avoir des fonctions configurant le timer/counter sur le port PB6 (celui-ci correspond au TIM4 channel 1). Voici comment se présente le code :

#define ESC_PPM_PERIOD 20000 // 50Hz

#define MIN_BLOWER_SPEED 300u

#define MAX_BLOWER_SPEED 1800u

#define DEFAULT_BLOWER_SPEED 900u

#define PIN_ESC_BLOWER | PB6 | // D10 / TIM4_CH1

#define TIM_CHANNEL_ESC_BLOWER 1 //Channel 1 de la pin D10

#define BlowerSpeed2MicroSeconds(value) map(value, 0, 1800, 1000, 1950) //Intervalle [1ms à 1,95 ms] sur la variation de vitesse du blower

#include "HardwareTimer.h"

HardwareTimer* hardwareTimer1; // Timer Blower command

hardwareTimer1 = new HardwareTimer(TIM4); //Sélectionne le timer 4 pour la pin D10 hardwareTimer1->setOverflow(ESC_PPM_PERIOD, MICROSEC_FORMAT); //Définit la période/fréquence de la PWM
hardwareTimer1->refresh(); //réninitialise le timer hardwareTimer1->setMode(TIM_CHANNEL_ESC_BLOWER, TIMER_OUTPUT_COMPARE_PWM1, PIN_ESC_BLOWER); //Permet de mettre le mode PWM sur le timer (Autres modes : Input Capture/Ouput Capture/Pulse Counter
// Set PPM width to 1ms
hardwareTimer1->setCaptureCompare(TIM_CHANNEL_ESC_BLOWER, BlowerSpeed2MicroSeconds(DEFAULT_BLOWER_SPEED), MICROSEC_COMPARE_FORMAT); //Définit le rapport cyclique de la PWM
hardwareTimer1->resume(); //Lance le timer
Figure 10 : Code de configuration du Timer/Counter

Avant de commencer, il est conseillé d’aller regarder la librairie « hardwareTimer.h » afin de voir toutes les méthodes de la librairie et les différents attributs (Voir Annexe 1). Nous allons décrire les différentes fonctions pour connaître leurs paramètres et rôles :

- HardwareTimer* hardwareTimer1 : Cette commande permet de faire appel à la librairie hardwareTimer.h à travers un objet. C’est grâce à cet objet que l’on va pouvoir utiliser les fonctions de la librarie « hardwareTimer »
- | hardwareTimer1 = new HardwareTimer(TIM4) | : Cette commande permet d’instancier l’objet
HardwareTimer en sélectionnant TIM4
- hardwareTimer1->setOverflow(ESC_PPM_PERIOD, MICROSEC_FORMAT) : Cette commande
permet de configurer la période du timer, dans notre cas ça va définir la période du signal PWM à 50 Hz.
- hardwareTimer1->refresh() : Cette commande met à jour tous les registres du timer
- hardwareTimer1->setMode(TIM_CHANNEL_ESC_BLOWER,TIMER_OUTPUT_COMPARE_PWM1,
PIN_ESC_BLOWER) : Cette commande permet de sélectionner le channel du timer, le mode du timer (PWM dans notre cas) et sur quel port (PB6).
- hardwareTimer1->setCaptureCompare(TIM_CHANNEL_ESC_BLOWER,
BlowerSpeed2MicroSeconds(DEFAULT_BLOWER_SPEED), | MICROSEC_COMPARE_FORMAT) | :
Cette commande permet de sélectionner le channel et définir le Flag (la limite) du timer. Cela va définir le rapport cyclique de notre signal PWM et donc de réaliser un signal PPM à laquelle son High Level Pulse va varier entre 1,06 ms et 1,86 ms (c’est BlowerSpeed2MicroSeconds qui va permettre cette variation)
- hardwareTimer1->resume() : Cette commande permet de lancer le timer et d’activer le channel du timer sélectionné.

En configurant tous les paramètres nécessaires, vous avez un signal PWM de 50 Hz qui est généré sur le port PB6. Vous pouvez modifier le rapport cyclique en variant la valeur dans BlowerSpeed2MicroSeconds. A présent, vous pouvez commander la vitesse du blower.

## Les différentes versions de la commande du Blower

Cette partie montre les différentes versions de la commande du Blower : Une commande simple du blower, la variation de la vitesse avec des boutons poussoirs.

### Commande simple

Vous pouvez retrouver le code en Annexe 2

Cette version est une commande simple du blower c’est-à-dire que l’on définit la vitesse de la turbine avant la compilation du code. Nous aurons juste un débit d’air envoyé constant.

### Variation de la vitesse

Vous pouvez retrouver le code en Annexe 3

Cette version est une commande permettant de varier la vitesse du blower avec des boutons poussoirs. On ajoute donc 2 boutons au système : un bouton pour augmenter la vitesse (PB10) et un bouton pour la diminuer (PA8). On ajoute une fonction anti-rebond à chaque bouton pour commander la turbine plus précisément et éviter les valeurs non désirées. Dans cette version nous ajoutons cette commande au timer :

- hardwareTimer1->attachInterrupt(TIM_CHANNEL_ESC_BLOWER,expiration) : Cette commande
permet de déclencher la fonction expiration à chaque fois que le timer atteint son Flag.

D’autres versions peuvent être ajoutées comme l’ajout d’un débitmètre ou encore le calcul du débit d’air envoyé par la turbine affiché sur un écran LCD.

## Annexe

### Annexe 1 : Librairie « hardwareTimer.h »

Définition des modes du timer :

typedef enum {
TIMER_DISABLED, | // == TIM_OCMODE_TIMING | no output, useful for only-
interrupt
// Output Compare
TIMER_OUTPUT_COMPARE, | // == Obsolete, use TIMER_DISABLED instead. Kept for
compatibility reason
TIMER_OUTPUT_COMPARE_ACTIVE, | // == TIM_OCMODE_ACTIVE | pin is set high when counter ==
channel compare
TIMER_OUTPUT_COMPARE_INACTIVE, | // == TIM_OCMODE_INACTIVE | pin is set low when counter ==
channel compare
TIMER_OUTPUT_COMPARE_TOGGLE, | // == TIM_OCMODE_TOGGLE | pin toggles when counter ==
channel compare
TIMER_OUTPUT_COMPARE_PWM1, | // == TIM_OCMODE_PWM1 | pin high when counter < channel
compare, low otherwise
TIMER_OUTPUT_COMPARE_PWM2, | // == TIM_OCMODE_PWM2 | pin low when counter < channel
compare, high otherwise
TIMER_OUTPUT_COMPARE_FORCED_ACTIVE, | // == TIM_OCMODE_FORCED_ACTIVE | pin always high
TIMER_OUTPUT_COMPARE_FORCED_INACTIVE, | // == TIM_OCMODE_FORCED_INACTIVE | pin always low

//Input capture
TIMER_INPUT_CAPTURE_RISING, | // == TIM_INPUTCHANNELPOLARITY_RISING
TIMER_INPUT_CAPTURE_FALLING, | // == TIM_INPUTCHANNELPOLARITY_FALLING
TIMER_INPUT_CAPTURE_BOTHEDGE, | // == TIM_INPUTCHANNELPOLARITY_BOTHEDGE

// Used 2 channels for a single pin. One channel in TIM_INPUTCHANNELPOLARITY_RISING another channel in TIM_INPUTCHANNELPOLARITY_FALLING.
// Channels must be used by pair: CH1 with CH2, or CH3 with CH4
// This mode is very useful for Frequency and Dutycycle measurement TIMER_INPUT_FREQ_DUTY_MEASUREMENT,

TIMER_NOT_USED = 0xFFFF // This must be the last item of this enum } TimerModes_t;

Définition des unités de la période du timer :

typedef enum {
TICK_FORMAT, // default
MICROSEC_FORMAT,
HERTZ_FORMAT,
} TimerFormat_t;

Définition du format pour configurer le rapport cyclique :

typedef enum {
TICK_COMPARE_FORMAT = 0x80, // default MICROSEC_COMPARE_FORMAT,
HERTZ_COMPARE_FORMAT,
PERCENT_COMPARE_FORMAT, // used for Dutycycle } TimerCompareFormat_t;

Méthodes importantes :

HardwareTimer(TIM_TypeDef *instance);
void resume(void); // Resume counter and all output channels
void refresh(void);
void setOverflow(uint32_t val, TimerFormat_t format = TICK_FORMAT); // set AutoReload register depending on format provided
void setMode(uint32_t channel, TimerModes_t mode, uint32_t pin);
void setCaptureCompare(uint32_t channel, uint32_t compare, TimerCompareFormat_t format = TICK_COMPARE_FORMAT); // set Compare register value of specified channel depending on format provided
void attachInterrupt(callback_function_t callback); // Attach interrupt callback which will be called upon update event (timer rollover)

### Annexe 2 : Code de la commande simple

#define ESC_PPM_PERIOD 20000 // 50Hz #define MIN_BLOWER_SPEED 300u

#define MAX_BLOWER_SPEED 1800u

#define DEFAULT_BLOWER_SPEED 900u

#define PIN_ESC_BLOWER | PB6 | // D10 / TIM4_CH1

#define TIM_CHANNEL_ESC_BLOWER 1 //Channel 1 de la pin D10

#define BlowerSpeed2MicroSeconds(value) map(value, 0, 1800, 1000, 1950) //Intervalle [1ms à 1,95 ms] sur la variation de vitesse du blower

#include "HardwareTimer.h"

HardwareTimer* hardwareTimer1; // Timer Blower command

void setup() {
// put your setup code here, to run once: PWM_Blower();
}

void PWM_Blower(){

pinMode(PIN_ESC_BLOWER, OUTPUT);
hardwareTimer1 = new HardwareTimer(TIM4); //Sélectionne le timer 4 pour la pin D10 hardwareTimer1->setOverflow(ESC_PPM_PERIOD, MICROSEC_FORMAT); //Définit la période/fréquence de la PWM
hardwareTimer1->refresh(); //réninitialise le timer hardwareTimer1->setMode(TIM_CHANNEL_ESC_BLOWER, TIMER_OUTPUT_COMPARE_PWM1, PIN_ESC_BLOWER); //Permet de mettre le mode PWM sur le timer (Autres modes : Input Capture/Ouput Capture/Pulse Counter
// Set PPM width to 1ms
hardwareTimer1->setCaptureCompare(TIM_CHANNEL_ESC_BLOWER, BlowerSpeed2MicroSeconds(DEFAULT_BLOWER_SPEED), MICROSEC_COMPARE_FORMAT); //Définit le rapport cyclique de la PWM
hardwareTimer1->resume(); //Lance le timer

}

### Annexe 3 : Variation de la Vitesse

#define ESC_PPM_PERIOD 20000 // 50Hz #define MIN_BLOWER_SPEED 300u

#define MAX_BLOWER_SPEED 1800u

#define DEFAULT_BLOWER_SPEED 900u

#define PIN_ESC_BLOWER | PB6 | // D10 / TIM4_CH1

#define TIM_CHANNEL_ESC_BLOWER 1 //Channel 1 de la pin D10

#define BlowerSpeed2MicroSeconds(value) map(value, 0, 1800, 1000, 1950) //Intervalle [1ms à 1,95 ms] sur la variation de vitesse du blower #include "HardwareTimer.h"

#include <LiquidCrystal.h>

HardwareTimer* hardwareTimer1; // Timer Blower command

LiquidCrystal lcd(PB3, PB4, PA9, PC7, PA7, PA6); //int i = 0;
static int speedBlower = DEFAULT_BLOWER_SPEED;

///////Debounce/////////
int reading, reading2 = 0;
int buttonState = 1; | | // the current reading from the input pin
int lastButtonState = 0; | // the previous reading from the input pin
int buttonState2 = 1; | | // the current reading from the input pin
int lastButtonState2 = 0; | // the previous reading from the input pin
// the following variables are unsigned longs because the time, measured in
// milliseconds, will quickly become a bigger number than can be stored in an int.
unsigned long lastDebounceTime = 50; | // the last time the output pin was toggled
unsigned long debounceDelay = 0; | // the debounce time; increase if the output
flickers
unsigned long lastDebounceTime2 = 50; // the last time the output pin was toggled

unsigned long debounceDelay2 = 0; | // the debounce time; increase if the output
flickers
////////////////////////

void setup() {
// put your setup code here, to run once: Serial.begin(115200);
lcd.begin(20, 4);
pinMode(PA8, INPUT_PULLUP); //D7 pinMode(PB10, INPUT_PULLUP); //D6 PWM_Blower();
}

void loop() {
// put your main code here, to run repeatedly: reading = digitalRead(PA8);
reading2 = digitalRead(PB10);
}

void PWM_Blower(){
pinMode(PIN_ESC_BLOWER, OUTPUT);
hardwareTimer1 = new HardwareTimer(TIM4); //Sélectionne le timer 4 pour la pin D10 hardwareTimer1->setOverflow(ESC_PPM_PERIOD, MICROSEC_FORMAT); //Définit la période/fréquence de la PWM
//hardwareTimer1->setOverflow(50, HERTZ_FORMAT);
hardwareTimer1->refresh(); //réninitialise le timer hardwareTimer1->setMode(TIM_CHANNEL_ESC_BLOWER, TIMER_OUTPUT_COMPARE_PWM1, PIN_ESC_BLOWER); //Permet de mettre le mode PWM sur le timer (Autres modes : Input Capture/Ouput Capture/One-pulse
// Set PPM width to 1ms
hardwareTimer1->setCaptureCompare(TIM_CHANNEL_ESC_BLOWER, BlowerSpeed2MicroSeconds(DEFAULT_BLOWER_SPEED), MICROSEC_COMPARE_FORMAT); //hardwareTimer1->setCaptureCompare(TIM_CHANNEL_ESC_BLOWER, 10 , PERCENT_COMPARE_FORMAT); //Définit le rapport cyclique de la PWM hardwareTimer1->attachInterrupt(TIM_CHANNEL_ESC_BLOWER,expiration); //Active la fonction à chaque interruption
hardwareTimer1->resume(); //Lance le timer
}

void expiration(){ if (reading != lastButtonState) { // reset the debouncing timer; lastDebounceTime = millis();; // if the button state has changed: if (reading != buttonState) { buttonState = reading;; if (buttonState == 0) { speedBlower -= 10;; } lastButtonState = reading;

if ((millis() - lastDebounceTime) > debounceDelay) {

// only toggle the LED if the new button state is HIGH

if (reading2 != lastButtonState2) { // reset the debouncing timer; lastDebounceTime2 = millis();; // if the button state has changed: if (reading2 != buttonState2) { buttonState2 = reading2;; if (buttonState2 == 0) { speedBlower += 10;

if ((millis() - lastDebounceTime2) > debounceDelay2) {

// only toggle the LED if the new button state is HIGH

}
}
lastButtonState2 = reading2; /*if (digitalRead(PA8) == 0) { speedBlower -= 10;
}
if (digitalRead(PB10) == 0) { speedBlower += 10;
}*/
if(speedBlower <= 100) | speedBlower = 100;
if(speedBlower >= 1800) | speedBlower = 1800;
lcd.setCursor(0,0);
lcd.print(speedBlower);
hardwareTimer1->setCaptureCompare(TIM_CHANNEL_ESC_BLOWER, BlowerSpeed2MicroSeconds(speedBlower), MICROSEC_COMPARE_FORMAT); hardwareTimer1->resume(); //Lance le timer
}

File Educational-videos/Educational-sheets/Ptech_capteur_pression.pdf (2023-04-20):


## BOUTRY Loan

### Alternant sur le projet MakAir


# Mesure avec un Capteur de pression

Ce document fait partie d’une série de livrables concernant la conception et le prototypage d’un respirateur à pression positive continue pour diminuer l’apnée du sommeil d’un patient

Ce livrable a pour but d’expliquer le fonctionnement du capteur de pression. La première partie du document est une analyse des caractéristiques du capteur. La deuxième partie portera sur la récupération des données de la mesure de la pression.

## Table des matières

Table des figures | 2
C’est quoi un Capteur de pression ? | 2
La communication I2C | 4
Récupération de la mesure de la pression | 5
Câblage du capteur | 6
Initialisation du capteur | 7
Récupération des données | 8
Annexe | 12

# Table des figures

Figure 1 : Les différents types de mesure d'une pression | 2
Figure 2 : Caractéristique du ABP2MRRT060MD2A3XX | 4
Figure 3 : Start/Stop bus I2C | 5
Figure 4 : Bus I2C du Capteur de pression ABP2 Series | 5
Figure 5 : Câblage du ABP2MRRT060MD2A3XX | 6
Figure 6 : Prototypage du capteur de pression | 7
Figure 7 : Code d'initialisation du capteur | 7
Figure 8 : Etape 1 de la communication I2C | 8
Figure 9 : Etape 3 de la communication I2C | 8
Figure 10 : Code de récupération des données en I2C | 9

# C’est quoi un Capteur de pression ?

La pression est définie comme la force appliquée par un liquide ou un gaz sur une surface et est généralement mesurée en unités de force par unité de surface. Les unités communes sont le Pascal (Pa), le Bar (barre), N / mm2 ou psi (livres par pouce carré). Par conséquent, un capteur de pression est un instrument composé à la fois d'un élément sensible à la pression pour déterminer la pression réelle appliquée au capteur et de certains composants pour convertir cette information en un signal de sortie. Pour adapter notre capteur à notre système, nous devons faire attention à certains paramètres :

- Type de mesure : Il y a 3 types de mesure avec un capteur de pression : absolue, relative et différentielle


Figure 1 : Les différents types de mesure d'une pression

- Les capteurs de pression absolue mesurent la pression par rapport à une
référence vide donc une pression à 0. Ils sont conçus avec | une référence qui
est une chambre fermée dans le capteur | (presque vide)
- Les capteurs de pression relative mesurent la pression par rapport à une pression de référence qui est la pression atmosphérique. Ils sont conçus avec une référence qui est l'air extérieur, grâce à un petit trou en dessous du capteur
- Les capteurs de pression différentielle mesurent la différence entre deux pressions, c’est souvent utilisé pour mesurer les niveaux de fluide et les débits. Ils sont conçus avec une référence qui est une autre sortie du capteur

Pour notre système (et en général dans le domaine médical), nous choisissons une mesure différentielle afin de comparer la pression interne et externe du système.
- Plage de mesure du capteur : c’est un paramètre important puisqu’il faut un capteur qui puisse mesurer toute la plage de pression de l’air que le système va produire. Il y a différentes unités liées à la pression comme nous avons pu le voir en introduction. Pour notre système, il est obligatoire d’avoir des valeurs négatives puisque la pression va être différente entre l’inspiration et l’expiration du patient
- La précision et répétabilité du capteur : ce sont des paramètres communs à tous les capteurs mais qui restent indispensable à prendre en compte. Les choix se font en fonction du domaine d’utilisation
- L’entrée du capteur : Il est important de savoir comment on va pouvoir mesurer une pression en faisant passer de l’air dans notre capteur. Pour un capteur différentiel, nous avons 2 entrées pour pouvoir insérer l’air externe et interne du système
- La tension nominale : C’est un paramètre plus spécifique à l’électronique, mais il est important de la savoir afin de connaître la tension que le système doit apporter au capteur de pression pour qu’il fonctionne correctement.
- La tension de sortie du capteur : Ce paramètre concerne la sécurité du microcontrôleur. Il faut faire attention à la tension maximale que peut sortir le capteur afin d’éviter d’endommager les pins (ex : pin STM32 = 3,3V max en entrée).
- Interface de communication : le dernier paramètre important, c’est la communication entre le microcontrôleur et le capteur de pression puisque c’est par cette voie que les données de la mesure vont être envoyées et reçues. Cela peut se faire avec une sortie analogique, une communication I2C ou encore une communication SPI. Dans notre cas, ça sera en communication I2C.

Pour la réalisation du respirateur PPC, nous prenons un capteur de pression différent du MakAir puisque celui n’est plus disponible chez les fournisseurs. Nous prenons le capteur de pression : ABP2MRRT060MD2A3XX. C’est un capteur de pression adapté au domaine médical et assez performant pour la mesure de la pression d’un respirateur PPC. Vous pouvez retrouver le choix technologique du capteur de pression en annexe afin d’avoir un exemple du procédé de recherche de capteurs. Pour notre capteur de pression, on peut retrouver sa caractéristique ci-dessous :


Figure 2 : Caractéristique du ABP2MRRT060MD2A3XX

Supply voltage | 3,3 Vdc
Précision | ± 0.25 %
Plage de mesure | -60 à 60 mbar
Communication | I2C

# La communication I2C

C’est un protocole de communication en série très commun en électronique qui a été développé au début des années 80 par Philips pour permettre de relier facilement à un microprocesseur les différents circuits d’un téléviseur moderne.

La communication I2C permet de faire communiquer entre eux des composants électronique très divers grâce à 3 signaux :
- Signal de donnée : SDA
- Signal d’horloge : SCL
- Signal de référence électrique : masse

Chaque protocole de communication communique grâce à bus et chaque bus comporte leurs caractéristiques. Les caractéristiques du bus I2C sont :
- 1 adresse unique pour chaque périphérique
- Bus multi-maître, détection des collisions et arbitrage
- Bus série, 8 bits, bidirectionnel à 100 kbps (standard mode), 400 kbps (fast mode), 3,2 Mbps (high-speed mode)

On peut décomposer le bus I2C comme cela :
- Le bus doit être au repos avant la prise de contrôle SDA et SCL à 1
- Pour transmettre des données, il faut surveiller :
- La condition de départ : SDA passe à 0, SCL reste à 1
- La condition d’arrêt : SDA passe à 1, SCL reste à 1

- Après avoir vérifié que le bus est libre, puis pris le contrôle de celui-ci, le circuit en devient le maître : c’est lui qui génère le signal d’horloge

Figure 3 : Start/Stop bus I2C

Sur un core Arduino, la communication I2C est gérée par la librairie Wire.h

Si l’on rentre dans la partie plus concrète de l’application de l’I2C dans un système. Chaque capteur a un bus I2C différent, c’est-à-dire que chaque octet du bus correspond à une donnée différente du capteur. On peut prendre en exemple le capteur de pression :


Figure 4 : Bus I2C du Capteur de pression ABP2 Series

Ce tableau explique les étapes à réaliser afin de récupérer les données du capteur. La première étape est la requête du Master au Slave. Cette étape permet d’initialiser le capteur par la communication I2C. La troisième étape est l’instant où le capteur envoie ses données au microcontrôleur, on peut voir qu’il y a 2 bus différents : un pour récupérer la pression seule et l’autre récupérer la pression et la température environnante. Petite remarque : on peut observer que le bus commence toujours par l’adressage du capteur par le Master, cela est obligatoire afin de reconnaître le capteur sur le bus I2C.

# Récupération de la mesure de la pression

Nous allons passer à la partie réalisation, nous allons voir comment récupérer la mesure de la pression de l’air envoyé.

Pour récupérer les données du capteur de pression en I2C, il y a plusieurs étapes à faire :
- Câblage du capteur : Cette étape se passe plutôt en Hardware puisqu’il consiste à câbler les pins du capteur sur des ports adaptés sur le microcontrôleur. Il suffit par la suite d’activer ces pins dans l’initialisation.
- Initialisation du capteur : Cette étape est importante pour débuter la communication entre le maître et l’esclave. On va donc configurer l’adresse du capteur et le bus I2C que doit recevoir le maître.

Récupération des données : Cette étape permet de récupérer le bus I2C et prendre les données communiquées par l’esclave. On peut aussi choisir si l’on intègre la fonction de mesure dans un loop() ou dans un timer configuré (cela dépend de l’application). La différence est non négligeable en fonction du système à concevoir :

- Loop() est un bloc du code qui va se répéter infiniment lorsque le système est en marche. C’est-à-dire que le code va être toujours être répété à chaque fin d’exécution du code. Cela peut être avantageux puisque le code sera toujours exécuté mais va être moins avantageux sur le temps d’exécution du système qui va augmenter.
- Un Timer est un élément configuré sur le microprocesseur afin qu’il réalise une ou des fonctions à chaque fois que le compteur (qui est configuré en fonction de la période du timer) a fini son décompte. Ce compteur s’incrémente en tâche du fond du code exécuté dans le loop(). Cela permet de réaliser des fonctions asynchrone au loop() à des périodes définies par le timer et donc d’optimiser le temps d’exécution du système.

## Câblage du capteur

La première étape est de se renseigner sur l’intégration Hardware du capteur de pression. Normalement toutes les informations sont présentes sur les datasheets des composants. Dans le cas du ABP2MRRT060MD2A3XX, on retrouve les différents pins (communication I2C) qui vont être reliés au microcontrôleur :


Figure 5 : Câblage du ABP2MRRT060MD2A3XX

GND : Ground/Masse | - | VDD : Voltage Drain (Positive Supply Voltage)
EOC : End-of-conversion indicator | - | NC : Not Connected
SDA : Serial Data Line | - | SCL : Serial Clock Line

EOC : Cette broche est mise à 1 lorsqu'une mesure et un calcul sont terminés

Il suffit donc de 5 fils pour câbler le capteur de pression. On peut l’ajouter au schéma de prototypage :


Figure 6 : Prototypage du capteur de pression

Maintenant le câblage réalisé, on peut passer à l’initialisation du capteur de pression

## Initialisation du capteur

La deuxième étape va permettre d’initialiser le capteur afin de préparer la communication I2C entre le maître et l’esclave. Cette étape est un protocole précis à mettre en place pour que la récupération des données se fassent correctement.
Avant de commencer, il est bien de préciser que l’on utilise la libraire « Wire.h » qui est la librairie la plus commune pour réaliser une communication I2C sur Arduino IDE. Chaque fonction sera expliquée au fur à mesure de la découverte du code. Voici le programme d’initialisation du capteur :

Wire.begin();

Wire.beginTransmission(id);
int stat = Wire.write (cmd, 3); // write command to the sensor stat |= Wire.endTransmission();
delay(10);
Wire.requestFrom(id, 7); // read back Sensor data 7 bytes

Figure 7 : Code d'initialisation du capteur

Nous allons analyser ce code en expliquant les différentes fonctions importantes pour l’initialisation :
- Wire.begin(); : Cette fonction permet de débuter une communication I2C, en général cette fonction est mise dans le « setup() »
- Wire.beginTransmission(id); : Cette fonction permet de faire une requête de transmission à l’esclave , id correspond à l’adresse I2C du capteur = 0x28

- Wire.write(cmd,3); : Cette fonction réalise la première étape de la récupération des données du capteur comme nous avons pu le voir précédemment :

Figure 8 : Etape 1 de la communication I2C

- Wire.endTransmission(); : Cette fonction permet de mettre fin à l’écriture et renvoie un message qui indique si la transmission est OK ou si il y a eu une erreur
- Wire.requestFrom(id, 7); : Cette fonction est une requête du maître pour que l’esclave lui envoie 7 octets de données (les 7 octets que l’on a pu analyser précédemment concernant la pression et la température). Cette fonction permet de définir la taille du bus I2C qui va être transmis

Maintenant que l’étape d’initialisation du capteur de pression est faite, on peut passer à la récupération de la mesure du capteur.

## Récupération des données

La troisième étape va permettre de récupérer les données du capteur de pression et va les traiter pour les rendre exploitables. On fait le choix de récupérer la pression et la température :

Figure 9 : Etape 3 de la communication I2C

Elle sous la forme d’une fonction que l’on peut mettre dans le loop() ou dans un timer. La différence est non négligeable en fonction du système à concevoir :

- Loop() est un bloc du code qui va se répéter infiniment lorsque le système est en marche. C’est-à-dire que le code va être toujours être répété à chaque fin d’exécution du code. Cela peut être avantageux puisque le code sera toujours exécuté mais va être moins avantageux sur le temps d’exécution du système qui va augmenter.
- Un Timer est un élément configuré sur le microprocesseur afin qu’il réalise une ou des fonctions à chaque fois que le compteur (qui est configuré en fonction de la période du timer) a fini son décompte. Ce compteur s’incrémente en tâche du fond du code exécuté dans le loop(). Cela permet de réaliser des fonctions asynchrone au loop() à des périodes définies par le timer et donc d’optimiser le temps d’exécution du système.

## Mise en place dans un loop()

Dans ce cas, on met cette fonction dans le loop().

void Pressure() {
Wire.beginTransmission(id);
int stat = Wire.write (cmd, 3); // write command to the sensor stat |= Wire.endTransmission();
delay(10);
Wire.requestFrom(id, 7); // read back Sensor data 7 bytes int i = 0;
for (i = 0; i < 7; i++) {
data [i] = Wire.read();
}
press_counts = data[3] + data[2] * 256 + data[1] * 65536; // calculate digital pressure counts
temp_counts = data[6] + data[5] * 256 + data[4] * 65536; // calculate digital temperature counts
temperature = (temp_counts * 200 / 16777215) - 50; // calculate temperature in deg c percentage = (press_counts / 16777215) * 100; // calculate pressure as percentage of full scale
//calculation of pressure value according to equation 2 of datasheet
pressure = ((press_counts - outputmin) * (pmax - pmin)) / (outputmax - outputmin) + pmin; dtostrf(press_counts, 4, 1, cBuff); // dtostrf() may be the function you need if you have a floating point value that you need to convert to a string.
dtostrf(percentage, 4, 3, percBuff);
dtostrf(pressure, 4, 3, pBuff);
dtostrf(temperature, 4, 3, tBuff);
/*
The below code prints the raw data as well as the processed data
Data format : Status Register, 24-bit Sensor Data, Digital Counts, percentage of full scale
pressure,
pressure output, temperature
*/
sprintf(printBuffer, " % x\t % 2x % 2x % 2x\t % s\t % s\t % s\t % s \n", data[0], data[1], data[2], data[3], cBuff, percBuff, pBuff, tBuff);
Serial.print(pBuff);
Serial.print(" KPa; ");
Serial.print(percBuff);
Serial.println(" % ");
delay(10);
}
Figure 10 : Code de récupération des données en I2C

On peut voir que les principales instructions réalisées sont le traitement des données lues, nous avons quand même la récupération des 7 octets de données par :

- Wire.read(); : Cette fonction est la lecture des données demandées à l’esclave. Cette fonction est limitée à 1 octet. C’est pour cela que l’on fait une boucle de 7 afin de récupérer tous les octets.

Comme dit précédemment, la suite concerne le traitement des données lues pour les rendre exploitable. Nous allons nous intéresser au traitement des données de la pression.

- press_counts = data[3] + data[2] * 256 + data[1] * 65536; : Cette formule permet
de mettre à l’échelle les données de pression lues.
- percentage = (press_counts / 16777215) * 100; : Cette formule permet de calculer la pression en pourcentage de la pleine échelle d’échantillonnage
- pressure = ((press_counts - outputmin) * (pmax - pmin)) / (outputmax -
outputmin) + pmin; : Cette formule permet de correspondre les données lues sur une unité de pression, nous pouvons donc avoir une pression avec une unité choisie, dans notre cas on met la pression en mbar. Pour modifier l’unité, il faut modifier les variables pmin et pmax. Cette formule est retrouvable sur la datasheet.

Toutes ces étapes permettent de récupérer la pression de l’air mesurée par le capteur. Le programme complet est en Annexe du livrable.

## Mise en place dans un Timer

Dans ce cas, on met la fonction dans un Timer pour la mettre en tâche de fond et de pouvoir gérer le temps d’activation de celle-ci. Les Timer/Counter ont généralement 4 modes d’utilisation : IC (Input Compare), OC (Output Compare), PWM et Pulse counter. C’est le mode OC qui nous intéresse dans notre cas puisque celui-ci va activer la fonction « Pressure » vue précédemment périodiquement (la période est définie par nous).

Pour utiliser le timer/counter sur le STM32F411RE, nous allons prendre la librairie « hardwareTimer » pour avoir des fonctions configurant le timer/counter. Voici comment se présente le code :

#define PRESSURE_PERIOD 200000 // 5Hz

#define TIM_CHANNEL_PRESSURE 2 //Channel 2 de la pin D3 #define PRESSURE_SDA PB3

#define PRESSURE_SCL PB10

#include<Wire.h>

#include "HardwareTimer.h"

HardwareTimer* hardwareTimer3; // Timer Pressure command

void setup() {

Serial.begin(115200);

while (!Serial) {
delay(10);
}

Wire.setSDA(PRESSURE_SDA); Wire.setSCL(PRESSURE_SCL);
Wire.begin();
Pressure_Timer();
sprintf(printBuffer, "\nStatus Register, 24 - bit Sensor data, Digital Pressure Counts,\ Percentage of full scale pressure, Pressure Output, Temperature\n"); Serial.println(printBuffer);

}

void loop() {

}

void Pressure_Timer() {
hardwareTimer3 = new HardwareTimer(TIM2); //Sélectionne le timer 4 pour la pin D10 hardwareTimer3->setOverflow(PRESSURE_PERIOD, MICROSEC_FORMAT); //Définit la période/fréquence de la PWM
hardwareTimer3->refresh(); //réninitialise le timer hardwareTimer3->setMode(TIM_CHANNEL_PRESSURE, TIMER_OUTPUT_COMPARE); //Permet de mettre le mode PWM sur le timer (Autres modes : Input Capture/Ouput Capture/One-pulse
// Set PPM width to 1ms
hardwareTimer3->setCaptureCompare(TIM_CHANNEL_PRESSURE, 0 , PERCENT_COMPARE_FORMAT); //Définit le rapport cyclique de la PWM hardwareTimer3->attachInterrupt(TIM_CHANNEL_PRESSURE, Pressure); //Active la fonction à chaque interruption
hardwareTimer3->resume(); //Lance le timer
}
Figure 11 : Code d'intégration d'un timer

Avant de commencer, il est conseillé d’aller regarder la librairie « hardwareTimer.h » afin de voir toutes les méthodes de la librairie et les différents attributs (Voir Annexe 1). Nous allons décrire les différentes fonctions pour connaître leurs paramètres et rôles :

- HardwareTimer* hardwareTimer3 : Cette commande permet de faire appel à la librairie hardwareTimer.h à travers un objet. C’est grâce à cet objet que l’on va pouvoir utiliser les fonctions de la librairie « hardwareTimer »
- | hardwareTimer3 = new HardwareTimer(TIM2) | : Cette commande permet d’instancier l’objet
HardwareTimer en sélectionnant TIM2
- hardwareTimer3->setOverflow(PRESSURE_PERIOD, MICROSEC_FORMAT) : Cette commande
permet de configurer la période du timer. Dans notre cas, ça va définir la période d’activation de la fonction à 5 Hz.
- hardwareTimer3->refresh() : Cette commande met à jour tous les registres du timer
- | hardwareTimer3->setMode(TIM_CHANNEL_PRESSURE,TIMER_OUTPUT_COMPARE) | : | Cette
commande permet de sélectionner le channel du timer et le mode du timer (OC dans notre cas)
- hardwareTimer3->setCaptureCompare(TIM_CHANNEL_PRESSURE,0,
PERCENT_COMPARE_FORMAT) : Cette commande permet de sélectionner le channel et le début du compteur.
- hardwareTimer3->resume() : Cette commande permet de lancer le timer et d’activer le channel du timer sélectionné.

En intégrant ce programme, notre fonction récupérant et traitant les données du capteur de pression s’activera tous les 0,2s. Notre programme du capteur de pression est donc fini.

# Annexe

Choix technologique du capteur de pression


Figure 12 : Choix technologique

Ce tableau a été créé afin de mettre en valeur la technologie de chaque capteur trouvé et de voir leurs avantages et inconvénients pour notre système. On compare aussi les caractéristiques importantes des capteurs pour voir lequel est le plus adapté à notre cas d’utilisation. On peut ajouter le prix et la disponibilité (non présent sur le tableau) pour savoir si le capteur répond au budget et s’il est disponible chez des fournisseurs de composants électronique

Programme du capteur de pression

#define PRESSURE_PERIOD 200000 // 5Hz

#define TIM_CHANNEL_PRESSURE 2 //Channel 2 de la pin D3 #define PRESSURE_SDA PB3

#define PRESSURE_SCL PB10

#include<Arduino.h>

#include<Wire.h>

#include "HardwareTimer.h"

HardwareTimer* hardwareTimer3; // Timer Pressure command

uint8_t id = 0x28; // i2c address
uint8_t data[7]; // holds output data
uint8_t cmd[3] = {0xAA, 0x00, 0x00}; // command to be sent double press_counts = 0; // digital pressure reading [counts] double temp_counts = 0; // digital temperature reading [counts] double pressure = 0; // pressure reading [bar, psi, kPa, etc.] double temperature = 0; // temperature reading in deg C
double outputmax = 15099494; // output at maximum pressure [counts] double outputmin = 1677722; // output at minimum pressure [counts]
double pmax = 60; // maximum value of pressure range [bar, psi, kPa, etc.] double pmin = -60; // minimum value of pressure range [bar, psi, kPa, etc.] double percentage = 0; // holds percentage of full scale data
char printBuffer[200], cBuff[20], percBuff[20], pBuff[20], tBuff[20];

void setup() {

Serial.begin(115200);

while (!Serial) {
delay(10);
}

Wire.setSDA(PRESSURE_SDA); Wire.setSCL(PRESSURE_SCL);
Wire.begin();
Pressure_Timer();
sprintf(printBuffer, "\nStatus Register, 24 - bit Sensor data, Digital Pressure Counts,\
Percentage of full scale pressure, Pressure Output, Temperature\n"); Serial.println(printBuffer);

}

void loop() {

}

void Pressure() {
Wire.beginTransmission(id);
int stat = Wire.write (cmd, 3); // write command to the sensor stat |= Wire.endTransmission();
delay(10);
Wire.requestFrom(id, 7); // read back Sensor data 7 bytes int i = 0;
for (i = 0; i < 7; i++) {
data [i] = Wire.read();
}

press_counts = data[3] + data[2] * 256 + data[1] * 65536; // calculate digital pressure counts
temp_counts = data[6] + data[5] * 256 + data[4] * 65536; // calculate digital temperature counts
temperature = (temp_counts * 200 / 16777215) - 50; // calculate temperature in deg c
percentage = (press_counts / 16777215) * 100; // calculate pressure as percentage of full scale
//calculation of pressure value according to equation 2 of datasheet pressure = ((press_counts - outputmin) * (pmax - pmin)) / (outputmax -outputmin) + pmin;
dtostrf(press_counts, 4, 1, cBuff); // dtostrf() may be the function you need if you have a floating point value that you need to convert to a string.
dtostrf(percentage, 4, 3, percBuff);
dtostrf(pressure, 4, 3, pBuff);
dtostrf(temperature, 4, 3, tBuff);
/*
The below code prints the raw data as well as the processed data Data format : Status Register, 24-bit Sensor Data, Digital Counts, percentage of full scale
pressure,
pressure output, temperature
*/
sprintf(printBuffer, " % x\t % 2x % 2x % 2x\t % s\t % s\t % s\t % s \n", data[0], data[1], data[2], data[3], cBuff, percBuff, pBuff, tBuff); Serial.print(pBuff);
Serial.print(" KPa; ");
Serial.print(percBuff);
Serial.println(" % ");
delay(10);
}

void Pressure_Timer() {
hardwareTimer3 = new HardwareTimer(TIM2); //Sélectionne le timer 4 pour la pin D10
hardwareTimer3->setOverflow(PRESSURE_PERIOD, MICROSEC_FORMAT); //Définit la période/fréquence de la PWM
hardwareTimer3->refresh(); //réninitialise le timer hardwareTimer3->setMode(TIM_CHANNEL_PRESSURE, TIMER_OUTPUT_COMPARE); //Permet de mettre le mode PWM sur le timer (Autres modes : Input Capture/Ouput Capture/One-pulse
// Set PPM width to 1ms
hardwareTimer3->setCaptureCompare(TIM_CHANNEL_PRESSURE, 0 , PERCENT_COMPARE_FORMAT); //Définit le rapport cyclique de la PWM hardwareTimer3->attachInterrupt(TIM_CHANNEL_PRESSURE, Pressure); //Active la fonction à chaque interruption
hardwareTimer3->resume(); //Lance le timer
}

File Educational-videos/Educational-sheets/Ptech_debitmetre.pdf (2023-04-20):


## BOUTRY Loan

### Alternant sur le projet MakAir


# Mesure avec un Débitmètre

Ce document fait partie d’une série de livrables concernant la conception et le prototypage d’un respirateur à pression positive continue pour diminuer l’apnée du sommeil d’un patient

Ce livrable a pour but d’expliquer le fonctionnement du débitmètre intégré dans le MakAir. La première partie du document est une analyse des caractéristiques du débitmètre. La deuxième partie portera sur la récupération des données de la mesure du débit d’air.

## Table des matières

Table des figures | 2
C’est quoi un débitmètre ? | 2
La communication I2C | 3
Récupération de la mesure du débit d’air | 4
Câblage du capteur | 5
Initialisation du capteur | 6
Récupération des données | 7
Mise en place dans le loop() | 8
Mise en place d’un Timer | 9
Annexe | 11

## Table des figures

Figure 1 : Caractéristiques du Honeywell Zephyr | 3
Figure 2 : Start/Stop bus I2C | 4
Figure 3 : Bus I2C du Honeywell Zephyr | 4
Figure 4 : Câblage du Honeywell Zephyr | 5
Figure 5 : Prototypage du débitmètre | 5
Figure 6 : Code d'initialisation du capteur | 6
Figure 7 : Code de récupération des données en I2C | 8
Figure 8 : Code d'intégration d'un timer | 9

# C’est quoi un débitmètre ?

Un débitmètre est un instrument utilisé pour mesurer le débit linéaire, non linéaire, massique ou volumétrique d'un liquide ou d'un gaz. Dans notre cas, nous voulons mesurer le débit d’air, donc nous allons nous porter vers des débitmètres plus adaptés dans ce domaine. Pour sélectionner un débitmètre, nous devons nous concentrer sur ces différents paramètres :
- Plage de mesure du capteur : c’est un paramètre important puisqu’il faut un capteur qui puisse mesurer toute la plage de débit d’air que le système va produire. Il y a différentes unités dans les fiches technique des débitmètres (SLPM, l/min, Cm³ /min).
- La pression nominale : c’est un paramètre important particulièrement dans notre cas puisque le système va produire de l’air avec une pression non négligeable, donc il faut que le débitmètre puisse supporter cette pression
- La précision et répétabilité du capteur : ce sont des paramètres communs à tous les capteurs mais qui restent indispensable à prendre en compte. Les choix se font en fonction du domaine d’utilisation
- La section d’installation : le débitmètre comporte un trou pour insérer un tuyau qui va transporter l’air envoyée. Il est important de prendre en compte quel tuyau nous allons utiliser et si le débitmètre est adapté à la section du tuyau pour pouvoir l’installer. Une différence trop importante de section entre le tuyau et le capteur pourrait créer une perte de charge, voire pire : des fortes turbulences sur l’écoulement d’air qui perturberaient la mesure
- La tension nominale d’alimentation : C’est un paramètre plus spécifique à l’électronique, mais il est important de la savoir afin de connaître la tension que le système doit apporter au débitmètre pour qu’il fonctionne correctement.

- Interface de communication : le dernier paramètre important, c’est la communication entre le microcontrôleur et le débitmètre puisque c’est par cette voie que les données de la mesure vont être envoyées et reçues. Cela peut se faire avec une sortie analogique, une communication I2C ou encore une communication SPI. Dans notre cas, ça sera en communication I2C.
- La technologie du capteur : fil chaud VS capteur différentiel

Pour la réalisation du respirateur PPC, nous restons sur le débitmètre d’inspiration du MakAir qui est le Honeywell Zephyr. C’est un débitmètre adapté au domaine médical et très performant pour la mesure d’un débit d’air. On peut retrouver ces différentes caractéristiques ci-dessous :


Figure 1 : Caractéristiques du Honeywell Zephyr

Supply voltage | 3,3 Vdc
Plage de débit | 0 - 200 SLPM
Résolution | 0,029 SLPM
Pression max | 60 Psi
Communication | I2C

# La communication I2C

C’est un protocole de communication en série très commun en électronique qui a été développé au début des années 80 par Philips pour permettre de relier facilement à un microprocesseur les différents circuits d’un téléviseur moderne.

La communication I2C permet de faire communiquer entre eux des composants électronique très divers grâce à 2 signaux :
- Signal de donnée : SDA
- Signal d’horloge : SCL

Chaque protocole de communication communique grâce à un bus et chaque bus comporte leurs caractéristiques. Les caractéristiques du bus I2C sont :
- 1 adresse unique pour chaque périphérique
- Bus multi-maître, détection des collisions et arbitrage
- Bus série, 8 bits, bidirectionnel à 100 kbps (standard mode), 400 kbps (fast mode), 3,2 Mbps (high-speed mode)

On peut décomposer le bus I2C comme cela :
- Le bus doit être au repos avant la prise de contrôle SDA et SCL à 1
- Pour transmettre des données, il faut surveiller :
- La condition de départ : SDA passe à 0, SCL reste à 1
- La condition d’arrêt : SDA passe à 1, SCL reste à 1
- Après avoir vérifié que le bus est libre, puis pris le contrôle de celui-ci, le circuit en devient le maître : c’est lui qui génère le signal d’horloge

Figure 2 : Start/Stop bus I2C

Sur un core Arduino, la communication I2C est gérée par la librairie Wire.h

Si l’on rentre dans la partie plus concrète de l’application de l’I2C dans un système. Chaque capteur a un bus I2C différent, c’est-à-dire que chaque octet du bus correspond à une donnée différente du capteur. On peut prendre exemple du débitmètre du MakAir :


Figure 3 : Bus I2C du Honeywell Zephyr

On peut voir que le bus commence par l’adresse du capteur pour le maître (microcontrôleur), ensuite un premier octet de donnée est envoyé et enfin un deuxième octet est envoyé. Le maître reçoit une donnée sur 16 bits. Ce bus comporte quelques particularités :
- SA : Mise à 0 de SDA par l’esclave
- MA : Mise à 0 de SDA par le maître
- MN : Mise à 1 de SDA par le maître pour l’arrêt de la trame

# Récupération de la mesure du débit d’air

Nous allons passer à la partie réalisation, nous allons voir comment récupérer la mesure du débit d’air grâce à un programme.

Pour récupérer les données du débitmètre en I2C, il y a plusieurs étapes à faire :
- Câblage du capteur : Cette étape se passe plutôt en Hardware puisqu’il consiste à câbler les pins du capteur sur des ports adaptés sur le microcontrôleur. Il suffit par la suite d’activer ces pins logiciellement dans l’initialisation.
- Initialisation du capteur : Cette étape est importante pour débuter la communication entre le maître et l’esclave. On va donc configurer l’adresse du capteur et le bus I2C que doit recevoir le maître.
- Récupération des données : Cette étape permet de récupérer le bus I2C et prendre les données communiquées par l’esclave. On peut aussi choisir si l’on intègre la fonction de mesure dans un loop() ou dans un timer configuré (cela dépend de l’application). Nous allons mettre en place ces 2 solutions.

## Câblage du capteur


La première étape est de se renseigner sur l’intégration Hardware du débitmètre. Normalement toutes les informations sont présentes sur les datasheets des composants. Dans le cas du Honeywell Zephyr, on retrouve les différents pins (communication I2C) qui vont être reliés au microcontrôleur :

Figure 4 : Câblage du Honeywell Zephyr

Il suffit donc de 4 fils pour câbler le débitmètre. On peut l’ajouter au schéma de prototypage :

Figure 5 : Prototypage du débitmètre

Maintenant le câblage réalisé, on peut passer à l’initialisation du débitmètre

## Initialisation du capteur

La deuxième étape va permettre d’initialiser le capteur afin de préparer la communication I2C entre le maître et l’esclave. Cette étape est un protocole bien précis à mettre en place pour que la récupération des données se fasse correctement.
Avant de commencer, il est bien de préciser que l’on utilise la libraire « Wire.h » qui est la librairie la plus commune pour réaliser une communication I2C sur Arduino IDE. Chaque fonction sera expliquée au fur à mesure de la découverte du code. Voici le programme d’initialisation du capteur :

////Constantes du programme////
#define MFM_HONEYWELL_HAF_I2C_ADDRESS 0x49 #define PIN_I2C_SDA PB9

#define PIN_I2C_SCL PB8

#include <Wire.h>

////Variables Débitmètre//// uint8_t slpm = 0;
int debit[2];
int32_t mfmInspiratoryLastValue = 0; int32_t mfmInspiratoryAirFlow = 0; union {
uint16_t i;
int16_t si;
unsigned char c[2];
} mfmLastData;

void setup() {
Serial.begin(115200);
Wire.setSDA(PIN_I2C_SDA);
Wire.setSCL(PIN_I2C_SCL);
Wire.begin();
sensor_Init();
PWM_Blower();
}

void sensor_Init(){ //lire le numéro de série

Wire.begin();
Wire.beginTransmission(MFM_HONEYWELL_HAF_I2C_ADDRESS); Wire.write(0x02); // Force reset
uint8_t txOk = Wire.endTransmission();
Wire.end();
delay(30); // délai necessaire pour séparer le cycle d’écriture et de lecture

uint32_t sn = 0;
Wire.begin();
Wire.beginTransmission(MFM_HONEYWELL_HAF_I2C_ADDRESS);
uint8_t rxcount = Wire.requestFrom(MFM_HONEYWELL_HAF_I2C_ADDRESS, 2); sn = Wire.read();
sn <<= 8;
sn |= Wire.read(); // first transmission is serial number register 0 sn <<= 8;
delay(2); // if you do not wait, sensor will send again register 0 rxcount += Wire.requestFrom(MFM_HONEYWELL_HAF_I2C_ADDRESS, 2);
sn |= Wire.read();
sn <<= 8;
sn |= Wire.read(); // second transmission is serial number register 1 Serial.print("Numéro de série : ");
Serial.println(sn);
Wire.end();
}
Figure 6 : Code d'initialisation du capteur

Nous allons analyser ce code en expliquant les différentes fonctions importantes pour l’initialisation :

- Wire.setSDA(PIN_I2C_SDA); / Wire.setSCL(PIN_I2C_SCL); : Ces fonctions permettent
de configurer les signaux SDA et SLC sur les pins PB9 et PB8
- Wire.begin(); : Cette fonction permet de débuter une communication I2C
- Wire.beginTransmission(MFM_HONEYWELL_HAF_I2C_ADDRESS); : Cette fonction permet de
faire une requête de transmission à l’esclave
- Wire.write(0x02); : Cette fonction permet au maître d’écrire à l’esclave, ici l’écriture d’un 0x02 permet de forcer le reset du capteur
- Wire.endTransmission(); : Cette fonction permet de mettre fin à l’écriture et renvoie un message qui indique si la transmission est OK ou si il y a eu une erreur
- Wire.end(); : Cette fonction permet de mettre fin à la communication I2C entre le maître et l’esclave.
- Wire.requestFrom(MFM_HONEYWELL_HAF_I2C_ADDRESS, 2); : Cette fonction est une
requête du maître pour que l’esclave lui envoie 2 octets de données (les 2 octets que l’on a pu précédemment concernant le Honeywell Zephyr). Cette fonction permet de définir la taille du bus I2C qui va être transmis
- Wire.read(); : Cette fonction est la lecture des données demandées à l’esclave. Cette fonction est limitée à 1 octet. C’est pour cela que l’on fait un décalage vers la gauche (sn <<=
8) afin d’éviter d’écraser l’octet reçu par le prochain octet qui va être reçu. Nous
recommençons l’opération de requête et de lecture une deuxième fois pour récupérer le deuxième registre du capteur afin d’avoir toutes les données du débitmètre.

On récupère à la fin de cette initialisation du capteur : son numéro de série qui est lui est propre lors de la communication I2C. Maintenant que les étapes d’initialisation du débitmètre est faite, on peut passer à la récupération de la mesure du capteur.

## Récupération des données

La troisième étape va permettre de récupérer les données du débitmètre et va les traiter pour les rendre exploitables. Elle est sous forme d’une fonction que l’on peut mettre dans le loop() ou dans un timer. La différence est non négligeable en fonction du système à concevoir :

- Loop() est un bloc du code qui va se répéter infiniment lorsque le système est en marche. C’est-à-dire que le code va être toujours être répété à chaque fin d’exécution du code. Cela peut être avantageux puisque le code sera toujours exécuté mais va être moins avantageux sur le temps d’exécution du système qui va augmenter.
- Un Timer est un élément configuré sur le microprocesseur afin qu’il réalise une ou des fonctions à chaque fois que le compteur (qui est configuré en fonction de la période du timer) a fini son décompte. Ce compteur s’incrémente en tâche du fond du code exécuté dans le loop(). Cela permet de réaliser des fonctions asynchrone au loop() à des périodes définies par le timer et donc d’optimiser le temps d’exécution du système.

## Mise en place dans le loop()

Dans ce cas, on met la fonction dans le loop().

void loop() {
airFlow();

}

void airFlow(){ //lire le débit
Wire.begin();
uint8_t readCount = Wire.requestFrom(MFM_HONEYWELL_HAF_I2C_ADDRESS, 2); mfmLastData.c[0] = Wire.read();
mfmLastData.c[1] = Wire.read();
// Wire.endTransmission() send a new write order followed by a stop. Useless and the
// sensor often nack it.
Wire.end();

mfmInspiratoryLastValue = (uint32_t)(mfmLastData.c[1] & 0xFFu); // masquage 0b00000000000000000000000011111111 & données du registre 1 (falcutatif) mfmInspiratoryLastValue |= (((uint32_t)mfmLastData.c[0]) << 8) & 0x0000FF00u; // masquage 0b00000000000000001111111100000000 & données du registre 0 (falcutatif)

// Theorical formula: Flow(slpm) = 200*((rawvalue/16384)-0.1)/0.8
// float implementation, 1 liter per minute unit
mfmInspiratoryAirFlow = 200 * (((uint32_t)mfmInspiratoryLastValue / 16384.0) - 0.1) / 0.8;
// (Output value in SLPM)

// fixed float implementation, 1 milliliter per minute unit //mfmInspiratoryAirFlow = (((10 * mfmInspiratoryLastValue) - 16384) * 1526); Serial.print("debit d'air : ");
Serial.print(mfmInspiratoryAirFlow);
Serial.println(" SLPM");
}
Figure 7 : Code de récupération des données en I2C

Nous retrouvons les fonctions « Wire » expliquaient précédemment, mais 2 formules sont mises en place et ont chacun leur utilité :

- | mfmInspiratoryLastValue = (uint32_t)(mfmLastData.c[1] & 0xFFu); | : Cette formule
est complexe à première vue mais est au final assez simple à comprendre. Le but ici est de faire un masquage (un ET avec 32 bits à 1 sur la données récupérée) sur une des cellules du tableau de données « mfmLastData.C », cela permet d’éviter de récupérer des données incohérentes
- mfmInspiratoryAirFlow = 200 * (((uint32_t)mfmInspiratoryLastValue / 16384.0)
- 0.1) / 0.8; : Cette formule est donnée dans la datasheet du capteur Honeywell Zephyr, elle permet de convertir la donnée reçue en une valeur de débit d’air (en SLPM).

Toutes ces étapes permettent de récupérer le débit d’air mesurée par le capteur.

## Mise en place d’un Timer

Dans ce cas, on met la fonction dans un Timer pour la mettre en tâche de fond et de pouvoir gérer le temps d’activation de celle-ci. Les Timer/Counter ont généralement 4 modes d’utilisation : IC (Input Compare), OC (Output Compare), PWM et Pulse counter. C’est le mode OC qui nous intéresse dans notre cas puisque celui-ci va activer la fonction « airflow » vue précédemment périodiquement (la période est définie par nous).

Pour utiliser le timer/counter sur le STM32F411RE, nous allons prendre la librairie « hardwareTimer » pour avoir des fonctions configurant le timer/counter. Voici comment se présente le code :

#define ESC_PPM_PERIOD 20000 // 50Hz #define AIRFLOW_PERIOD 200000 // 5Hz #define MIN_BLOWER_SPEED 300u

#define MAX_BLOWER_SPEED 1800u

#define DEFAULT_BLOWER_SPEED 900u

#define PIN_ESC_BLOWER | PB6 | // D10 / TIM4_CH1

#define TIM_CHANNEL_ESC_BLOWER 1 //Channel 1 de la pin D10

#define TIM_CHANNEL_AIRFLOW 4 //Channel 4 de la pin D15

#define BlowerSpeed2MicroSeconds(value) map(value, 0, 1800, 1000, 1950) //Intervalle [1ms à 1,95 ms] sur la variation de vitesse du blower

#define MFM_HONEYWELL_HAF_I2C_ADDRESS 0x49

#define PIN_I2C_SDA PB9

#define PIN_I2C_SCL PB8

#include <Wire.h>

#include "HardwareTimer.h"

HardwareTimer* hardwareTimer1; | // Timer Blower command
HardwareTimer* hardwareTimer2; | // Timer Debitmetre command

void setup() {
Serial.begin(115200);
Wire.setSDA(PIN_I2C_SDA);
Wire.setSCL(PIN_I2C_SCL);
Wire.begin();
sensor_Init();
PWM_Blower();
Airflow_Timer();
}

void loop() {

}

void Airflow_Timer() {
hardwareTimer2 = new HardwareTimer(TIM1); //Sélectionne le timer 4 pour la pin D10 hardwareTimer2->setOverflow(AIRFLOW_PERIOD, MICROSEC_FORMAT); //Définit la période/fréquence de la PWM
hardwareTimer2->refresh(); //réninitialise le timer hardwareTimer2->setMode(TIM_CHANNEL_AIRFLOW, TIMER_OUTPUT_COMPARE); //Permet de mettre le mode PWM sur le timer (Autres modes : Input Capture/Ouput Capture/One-pulse
// Set PPM width to 1ms
hardwareTimer2->setCaptureCompare(TIM_CHANNEL_AIRFLOW, 0 , PERCENT_COMPARE_FORMAT); //Définit le rapport cyclique de la PWM
hardwareTimer2->attachInterrupt(TIM_CHANNEL_AIRFLOW, airFlow); //Active la fonction à chaque interruption
hardwareTimer2->resume(); //Lance le timer
}
Figure 8 : Code d'intégration d'un timer

Avant de commencer, il est conseillé d’aller regarder la librairie « hardwareTimer.h » afin de voir toutes les méthodes de la librairie et les différents attributs (Voir Annexe 1). Nous allons décrire les différentes fonctions pour connaître leurs paramètres et rôles :

- HardwareTimer* hardwareTimer2 : Cette commande permet de faire appel à la librairie hardwareTimer.h à travers un objet. C’est grâce à cet objet que l’on va pouvoir utiliser les fonctions de la librairie « hardwareTimer »
- | hardwareTimer2 = new HardwareTimer(TIM1) | : Cette commande permet d’instancier l’objet
HardwareTimer en sélectionnant TIM1
- hardwareTimer2->setOverflow(AIRFLOW_PERIOD, MICROSEC_FORMAT) : Cette commande
permet de configurer la période du timer. Dans notre cas, ça va définir la période d’activation de la fonction à 5 Hz.
- hardwareTimer2->refresh() : Cette commande met à jour tous les registres du timer
- | hardwareTimer2->setMode(TIM_CHANNEL_AIRFLOW,TIMER_OUTPUT_COMPARE) | : | Cette
commande permet de sélectionner le channel du timer et le mode du timer (OC dans notre cas)
- hardwareTimer2->setCaptureCompare(TIM_CHANNEL_AIRFLOW,0,
PERCENT_COMPARE_FORMAT) : Cette commande permet de sélectionner le channel et le début du compteur.
- hardwareTimer2->resume() : Cette commande permet de lancer le timer et d’activer le channel du timer sélectionné.

En intégrant ce programme, notre fonction récupérant et traitant les données du débitmètre s’activera tous les 0,2s. Notre programme du débitmètre est donc fini.

# Annexe

#define ESC_PPM_PERIOD 20000 // 50Hz #define AIRFLOW_PERIOD 200000 // 5Hz #define MIN_BLOWER_SPEED 300u

#define MAX_BLOWER_SPEED 1800u

#define DEFAULT_BLOWER_SPEED 900u

#define PIN_ESC_BLOWER | PB6 | // D10 / TIM4_CH1

#define TIM_CHANNEL_ESC_BLOWER 1 //Channel 1 de la pin D10

#define TIM_CHANNEL_AIRFLOW 4 //Channel 4 de la pin D15

#define BlowerSpeed2MicroSeconds(value) map(value, 0, 1800, 1000, 1950) //Intervalle [1ms à 1,95 ms] sur la variation de vitesse du blower #define MFM_HONEYWELL_HAF_I2C_ADDRESS 0x49

#define PIN_I2C_SDA PB9

#define PIN_I2C_SCL PB8

#include <Wire.h>

#include "HardwareTimer.h"

HardwareTimer* hardwareTimer1; | // Timer Blower command
HardwareTimer* hardwareTimer2; | // Timer Debitmetre command

////Variables Blower////
static int speedBlower = MAX_BLOWER_SPEED;

////Variables Débitmètre////
uint8_t slpm = 0;
int debit[2];
int32_t mfmInspiratoryLastValue = 0; int32_t mfmInspiratoryAirFlow = 0; union {
uint16_t i;
int16_t si;
unsigned char c[2];
} mfmLastData;

void setup() {
Serial.begin(115200);
Wire.setSDA(PIN_I2C_SDA);
Wire.setSCL(PIN_I2C_SCL);
Wire.begin();
sensor_Init();
PWM_Blower();
Airflow_Timer();
}

void loop() {

}

void airFlow() { //lire le débit
Wire.begin();
uint8_t readCount = Wire.requestFrom(MFM_HONEYWELL_HAF_I2C_ADDRESS, 2); mfmLastData.c[0] = Wire.read();
mfmLastData.c[1] = Wire.read();
// Wire.endTransmission() send a new write order followed by a stop. Useless and the
// sensor often nack it.
Wire.end();

mfmInspiratoryLastValue = (uint32_t)(mfmLastData.c[1] & 0xFFu); // masquage 0b00000000000000000000000011111111 & données du registre 1 (falcutatif)
mfmInspiratoryLastValue |= (((uint32_t)mfmLastData.c[0]) << 8) & 0x0000FF00u; // masquage 0b00000000000000001111111100000000 & données du registre 0 (falcutatif)

// Theorical formula: Flow(slpm) = 200*((rawvalue/16384)-0.1)/0.8
// float implementation, 1 liter per minute unit mfmInspiratoryAirFlow = 200 * (((uint32_t)mfmInspiratoryLastValue / 16384.0) - 0.1) / 0.8;
// (Output value in SLPM)

// fixed float implementation, 1 milliliter per minute unit //mfmInspiratoryAirFlow = (((10 * mfmInspiratoryLastValue) - 16384) * 1526);
Serial.print("debit d'air : ");
Serial.print(mfmInspiratoryAirFlow);
Serial.println(" SLPM");
}
void sensor_Init() { //lire le numéro de série

Wire.begin();
Wire.beginTransmission(MFM_HONEYWELL_HAF_I2C_ADDRESS); Wire.write(0x02); // Force reset
uint8_t txOk = Wire.endTransmission();
Wire.end();
delay(30);

uint32_t sn = 0;
Wire.begin();
Wire.beginTransmission(MFM_HONEYWELL_HAF_I2C_ADDRESS);
uint8_t rxcount = Wire.requestFrom(MFM_HONEYWELL_HAF_I2C_ADDRESS, 2); sn = Wire.read();
sn <<= 8;
sn |= Wire.read(); // first transmission is serial number register 0 sn <<= 8;
delay(2); // if you do not wait, sensor will send again register 0 rxcount += Wire.requestFrom(MFM_HONEYWELL_HAF_I2C_ADDRESS, 2);
sn |= Wire.read();
sn <<= 8;
sn |= Wire.read(); // second transmission is serial number register 1 Serial.print("Numéro de série : ");
Serial.println(sn);
Wire.end();
}

void PWM_Blower() {
pinMode(PIN_ESC_BLOWER, OUTPUT);
hardwareTimer1 = new HardwareTimer(TIM4); //Sélectionne le timer 4 pour la pin D10
hardwareTimer1->setOverflow(ESC_PPM_PERIOD, MICROSEC_FORMAT); //Définit la période/fréquence de la PWM
//hardwareTimer1->setOverflow(50, HERTZ_FORMAT); hardwareTimer1->refresh(); //réninitialise le timer hardwareTimer1->setMode(TIM_CHANNEL_ESC_BLOWER, TIMER_OUTPUT_COMPARE_PWM1, PIN_ESC_BLOWER); //Permet de mettre le mode PWM sur le timer (Autres modes : Input Capture/Ouput Capture/One-pulse
// Set PPM width to 1ms
hardwareTimer1->setCaptureCompare(TIM_CHANNEL_ESC_BLOWER, BlowerSpeed2MicroSeconds(DEFAULT_BLOWER_SPEED), MICROSEC_COMPARE_FORMAT);

//hardwareTimer1->setCaptureCompare(TIM_CHANNEL_ESC_BLOWER, 10 , PERCENT_COMPARE_FORMAT); //Définit le rapport cyclique de la PWM hardwareTimer1->resume(); //Lance le timer
}

void Airflow_Timer() {
hardwareTimer2 = new HardwareTimer(TIM1); //Sélectionne le timer 4 pour la pin D10
hardwareTimer2->setOverflow(AIRFLOW_PERIOD, MICROSEC_FORMAT); //Définit la période/fréquence de la PWM
hardwareTimer2->refresh(); //réninitialise le timer hardwareTimer2->setMode(TIM_CHANNEL_AIRFLOW, TIMER_OUTPUT_COMPARE); //Permet de mettre le mode PWM sur le timer (Autres modes : Input Capture/Ouput Capture/One-pulse
// Set PPM width to 1ms
hardwareTimer2->setCaptureCompare(TIM_CHANNEL_AIRFLOW, 0 , PERCENT_COMPARE_FORMAT); //Définit le rapport cyclique de la PWM hardwareTimer2->attachInterrupt(TIM_CHANNEL_AIRFLOW, airFlow); //Active la fonction à chaque interruption
hardwareTimer2->resume(); //Lance le timer
}

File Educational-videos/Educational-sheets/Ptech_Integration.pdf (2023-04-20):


# BOUTRY Loan

# Alternant sur le projet MakAir


# Intégration du système

Ce document fait partie d’une série de livrables concernant la conception et le prototypage

## d’un respirateur à pression positive continue pour diminuer l’apnée du sommeil d’un patient

Ce livrable a pour but d’expliquer l’intégration des composants du système afin d’avoir une fonction générale du système qui consiste à envoyer de l’air en continu.

# Table des matières

## Table des figures | 2

## C’est quoi une intégration ? | 2

## Les étapes de l’intégration | 3

## Etape 1 : Adapter les différents programmes et l’assembler | 3

## Etape 2 : Modifier le programme | 5

## Etape finale : Tests unitaires | 6

## Etape bonus : Création de fichier .h et .cpp | 8

## Annexe | 11

# Table des figures

Figure 1 : Intégration des composants du Respirateur PPC | 2 Figure 2 : Test unitaire du débitmètre | 6 Figure 3 : Test unitaire du blower | 7 Figure 4 : Test unitaire du capteur de pression | 7 Figure 5 : Test unitaire de l'afficheur LCD | 8 Figure 6 : création des 2 fichiers .h et .cpp | 8 Figure 7 : Fichier .h | 9 Figure 8 : fichier .cpp | 9 Figure 9 : Dossier du composant programmé | 10 Figure 10 : Programme principal | 10

# C’est quoi une intégration ?

L’intégration lors d’un projet consiste à réunir au sein d'un même système, (https://fr.wikipedia.org/wiki/Syst%C3%A8me_d%27information) des parties

## développées de façon séparées. Cette partie est très importante puisqu’elle va être votre

structure finale de votre système. Il est important de faire attention à chaque fonction intégrée, d’ensuite d’adapter toutes les fonctions et d’enfin faire des tests unitaires pour savoir si chaque fonction du système fonctionne. En règle générale, cette partie va être la plus longue s’il n’y a

## pas eu de réflexion d’adaptabilité de chaque fonction. Nous allons voir les étapes de

l’intégration.


### Figure 1 : Intégration des composants du Respirateur PPC

# Les étapes de l’intégration

Nous allons avoir 4 étapes lors de cette intégration : Adapter les différentes fonctions, assembler les fonctions sur un programme, Ajuster le programme pour avoir un résultat final et réaliser des tests unitaires sur chaque fonction.

# Etape 1 : Adapter les différents programmes et l’assembler

## La première étape est de modifier les différents programmes du système pour éviter des erreurs de variables, d’association de pins ou encore des fonctions ambigües. Nous allons montrer quelques exemples d’adaptation à réaliser :

## - HardwareTimer : Activer des timers différents pour chaque composant du système

HardwareTimer* hardwareTimer1; | // Timer Blower command
HardwareTimer* hardwareTimer2; | // Timer Debitmetre command
HardwareTimer* hardwareTimer3; | // Timer Pressure command

Ici on peut voir que l’on crée 3 timers afin de séparer le Blower, le débitmètre et le capteur de pression. Cela va permettre de gérer la périodicité de chaque composant et de pouvoir gérer

## leur mode d’activation. En réalisant cette manipulation, il faut donc prendre en compte différents timers et channels du microcontrôleur :

hardwareTimer1 = new HardwareTimer(TIM4); //Sélectionne le timer 4 hardwareTimer2 = new HardwareTimer(TIM1); //Sélectionne le timer 1 hardwareTimer3 = new HardwareTimer(TIM2); //Sélectionne le timer 2

#define TIM_CHANNEL_ESC_BLOWER 1 //Channel 1 de la pin D10 #define TIM_CHANNEL_AIRFLOW 4 //Channel 4 de la pin D15

#define TIM_CHANNEL_PRESSURE 2 //Channel 2 de la pin D3

## On associe différents timers pour éviter des confusions pour le microprocesseur et qu’une

erreur se produise lors de l’exécution du code. Ensuite les channels sont choisis en fonction de l’association de la pin (voir la fiche pédagogique du Blower). En séparant les différentes fonctions et les timers associées, on va éviter des erreurs d’activation des composants.

## - Communication I2C multi-slaves : Mettre en place une communication I2C avec un maître et deux esclaves (débitmètre et capteur de pression)

//Communication I2C multi-slaves
TwoWire myWire1(PIN_I2C_SDA, PIN_I2C_SCL); TwoWire myWire2(PRESSURE_SDA, PRESSURE_SCL);

Cette manipulation se fait avec la fonction TwoWire qui permet de créer plusieurs slaves dans

## une communication I2C, cela va donc remplacer l’objet commun « Wire » par « myWire1 » et

« myWire2 » qui vont chacun représenter un composant : débitmètre et capteur de pression.

## Ensuite, on met en place le remplacement dans chaque fonction :

myWire1.begin(); //Initialisation de la communication I2C avec le débitmètre myWire2.begin();//Initialisation de la communication I2C avec le capteur de pression

## On remarque qu’il n’y a plus besoin de la fonction Wire.setSDA et Wire.setSCL puisque les

pins sont déjà associés au moment de la création de l’objet TwoWire.

## Voici un exemple d’une partie du code « sensor_Init() » avec l’objet myWire1 :

myWire1.begin();
myWire1.beginTransmission(MFM_HONEYWELL_HAF_I2C_ADDRESS); myWire1.write(0x02); // Force reset
uint8_t txOk = myWire1.endTransmission();
myWire1.end();

## Un autre exemple avec une partie du code « Pressure() » avec l’objet myWire2 :

myWire2.beginTransmission(id);
int stat = myWire2.write (cmd, 3); // write command to the sensor
stat |= myWire2.endTransmission();
delay(10);
myWire2.requestFrom(id, 7); // read back Sensor data 7 bytes

## Après avoir modifier toutes les fonctions concernant la communication I2C, vous pouvez

communiquer avec 2 slaves.
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

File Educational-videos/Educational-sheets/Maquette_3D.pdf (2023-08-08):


## BOUTRY Loan

### Alternant sur le projet MakAir

# Maquette 3D

Ce document fait partie d’une série de livrables concernant la conception et le prototypage d’un respirateur à pression positive continue pour diminuer l’apnée du sommeil d’un patient

Ce livrable a pour but d’expliquer la modélisation de pièce 3D, de la configuration pour l’impression de la pièce et des différentes versions de la maquette du respirateur contre l’apnée du sommeil. Cette partie concernera un autre domaine de l’ingénierie : La modélisation 3D
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

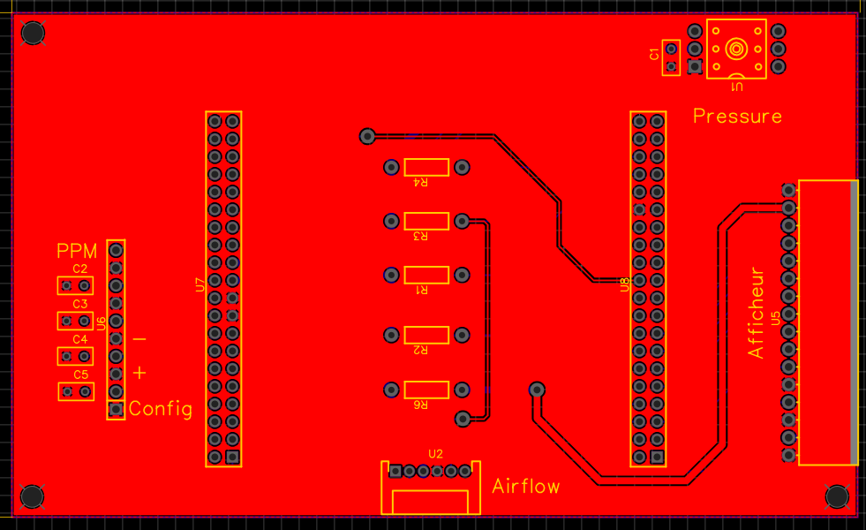
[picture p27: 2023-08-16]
Motherboard-CPAP/Top_PCB.png

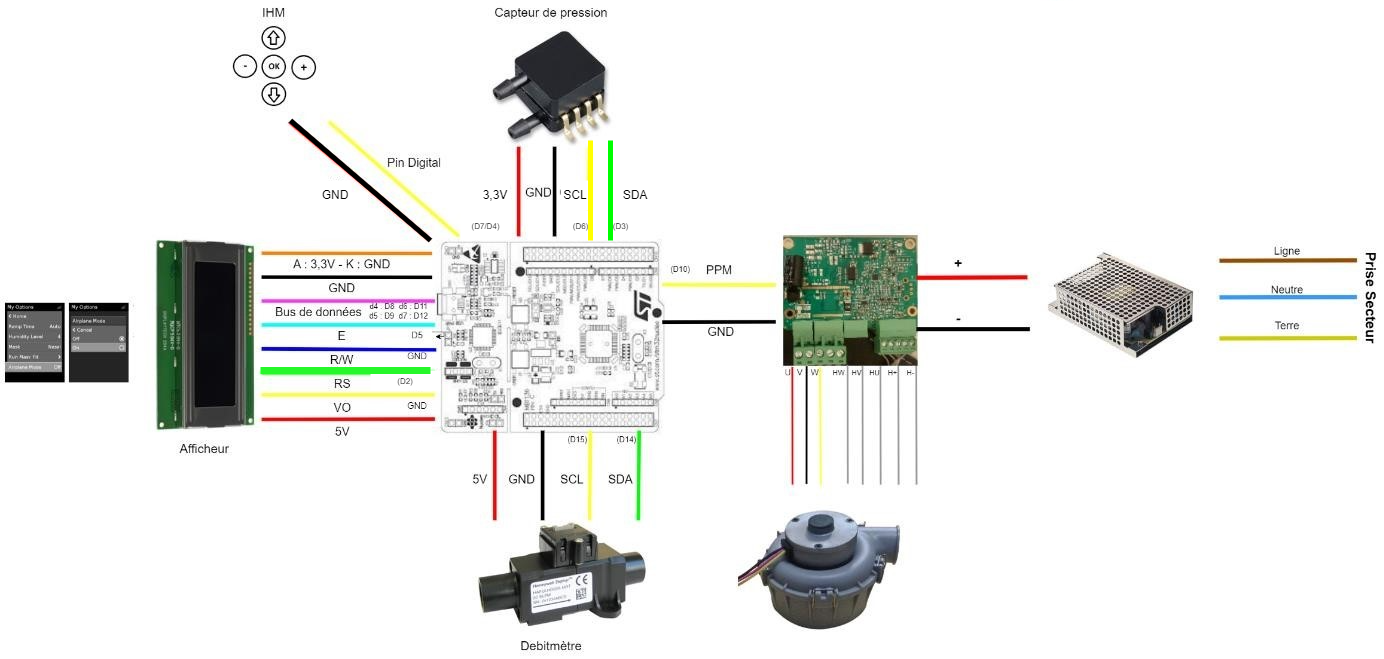
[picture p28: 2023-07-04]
Various-CPAP/Circuit_prototypage.png

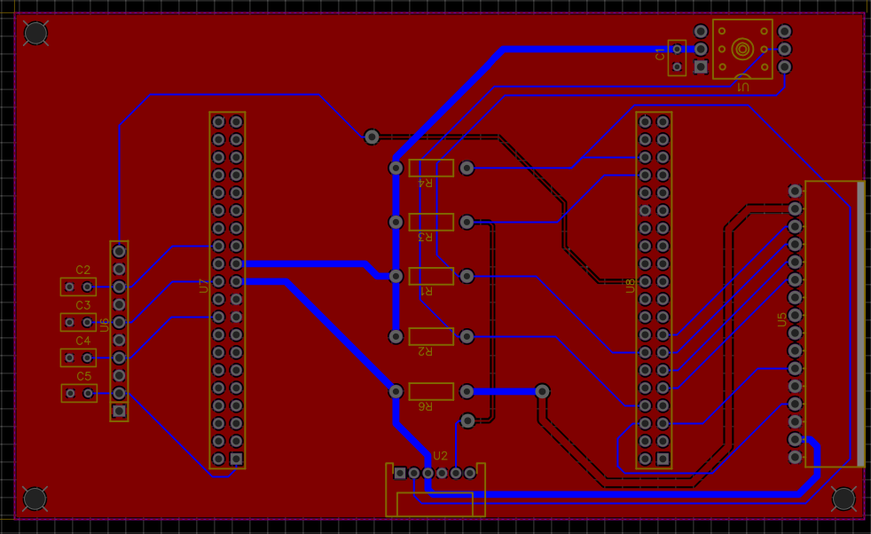
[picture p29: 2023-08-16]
Motherboard-CPAP/Bottom_PCB.png

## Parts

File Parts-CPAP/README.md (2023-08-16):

## Accessories

These are the parts that mechanically complete the different functional blocks of the system

[FreeCAD](https://github.com/makers-for-life/makair-cpap/blob/master/Parts-CPAP/Accessories/Accessories.FCStd)

| Part  | Version | Improvement | Ready? | STL file |
| ------------- | ------------- | ------------- | ------------- | ------------- |
| Adaptateur Blower&Debitmetre | V1 |  | ✅ | [STL](https://github.com/makers-for-life/makair-cpap/blob/master/Parts-CPAP/Accessories/Adaptateur_Blower_Debitmetre.stl) |
|  Fermeture avant-Attache 20cm (1) | V1 |  | ✅ | [STL](https://github.com/makers-for-life/makair-cpap/blob/master/Parts-CPAP/Accessories/Fermeture_avant-Attache.stl) |
|  Fermeture avant-Attache 10cm (2) | V1 |  | ✅ | [STL](https://github.com/makers-for-life/makair-cpap/blob/master/Parts-CPAP/Accessories/Fermeture_avant-Attache2.stl) |
|  Oxygen Mixer | V1 |  | ✅ | [STL](https://github.com/makers-for-life/makair-cpap/blob/master/Parts-CPAP/Accessories/Oxygen_Mixer.stl) |
|  Pièce d'alimentation | V1 |  | ✅ | [STL](https://github.com/makers-for-life/makair-cpap/blob/master/Parts-CPAP/Accessories/Piece_Alim.stl) |
|  Sortie Respirateur | V1 |  | ✅ | [STL](https://github.com/makers-for-life/makair-cpap/blob/master/Parts-CPAP/Accessories/Sortie_respirateur.stl) |

## Blower Holder

This part is taken from the MakAir [Blower Holder](https://github.com/makers-for-life/makair-parts/tree/master/src/blower-holder)

## Case

This file contains all the parts of the CPAP ventilator case

[FreeCAD](https://github.com/makers-for-life/makair-cpap/blob/master/Parts-CPAP/Case/Bo%C3%AEtier.FCStd)

| Part  | Version | Improvement | Ready? | STL file | 2nd file |
| ------------- | ------------- | ------------- | ------------- | ------------- | ------------- |
| 3 Pcs | [V1](https://github.com/makers-for-life/makair-cpap/tree/master/Parts-CPAP/Case/3Pcs-V1) |  | ✅ | |
| 3 Pcs  | [V2](https://github.com/makers-for-life/makair-cpap/tree/master/Parts-CPAP/Case/3Pcs-V2) | Adjustment of the Blower location + Improvement of the HMI | ✅ | |
| 5 Pcs  | [V1](https://github.com/makers-for-life/makair-cpap/tree/master/Parts-CPAP/Case/5Pcs-V1) |  | ✅ | |
| 5 Pcs | [V2](https://github.com/makers-for-life/makair-cpap/tree/master/Parts-CPAP/Case/5Pcs-V2) | Adjustment of the Blower location + Improvement of the HMI | ✅ | |
|  Base | V1 |  | ✅ | [STL](https://github.com/makers-for-life/makair-cpap/blob/master/Parts-CPAP/Case/Base_1.stl) | [STL](https://github.com/makers-for-life/makair-cpap/blob/master/Parts-CPAP/Case/Base_2.stl)
|  1er étage | V1 |  | ✅ | [STL](https://github.com/makers-for-life/makair-cpap/blob/master/Parts-CPAP/Case/1er_etage_1.stl) | [STL](https://github.com/makers-for-life/makair-cpap/blob/master/Parts-CPAP/Case/1er_etage_2.stl)
|  Sortie | V1 |  | ✅ | [STL](https://github.com/makers-for-life/makair-cpap/blob/master/Parts-CPAP/Case/Fa%C3%A7ade_Sortie.stl) |
|  Alimentation | V1 |  | ✅ | [STL](https://github.com/makers-for-life/makair-cpap/blob/master/Parts-CPAP/Case/Fa%C3%A7ade_alim.stl) |
|  Avant | V1 |  | ✅ | [STL](https://github.com/makers-for-life/makair-cpap/blob/master/Parts-CPAP/Case/Fa%C3%A7ade_avant1.stl) | [STL](https://github.com/makers-for-life/makair-cpap/blob/master/Parts-CPAP/Case/Fa%C3%A7ade_avant2.stl)
|  Arrière | V1 |  | ✅ | [STL](https://github.com/makers-for-life/makair-cpap/blob/master/Parts-CPAP/Case/Fa%C3%A7ade_arriere_1.stl) | [STL](https://github.com/makers-for-life/makair-cpap/blob/master/Parts-CPAP/Case/Fa%C3%A7ade_arriere_2.stl)
|  Fermeture | V1 |  | ✅ | [STL](https://github.com/makers-for-life/makair-cpap/blob/master/Parts-CPAP/Case/Fermeture_1.stl) | [STL](https://github.com/makers-for-life/makair-cpap/blob/master/Parts-CPAP/Case/Fermeture_2.stl)
|  Renfort | V1 |  | ✅ | [STL](https://github.com/makers-for-life/makair-cpap/blob/master/Parts-CPAP/Case/Renfort_Base.stl) |

| Part  | Version | Improvement | Ready? | Reference | Pictures |
| ------------- | ------------- | ------------- | ------------- | ------------- | ------------- |
| Case | V2 | New casing | ✅ | [ABS case](https://fr.rs-online.com/web/p/boitiers-pour-usage-general/7739651) | [IHM /](https://github.com/makers-for-life/makair-cpap/blob/f39e4fc76240c4e0c32e0eeabd5b6c42e856a4f0/Parts-CPAP/Case_V2/IHM.jpg) [Input /](https://github.com/makers-for-life/makair-cpap/blob/f39e4fc76240c4e0c32e0eeabd5b6c42e856a4f0/Parts-CPAP/Case_V2/Input.jpg) [Output](https://github.com/makers-for-life/makair-cpap/blob/f39e4fc76240c4e0c32e0eeabd5b6c42e856a4f0/Parts-CPAP/Case_V2/Output.jpg) |

## Filter Box

This part is taken from the MakAir [Filter Box](https://github.com/makers-for-life/makair-parts/tree/master/src/machine-filter-box)

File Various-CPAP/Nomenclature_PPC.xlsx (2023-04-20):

Elément du respirateur | Référence du produit | Quantité | Prix unitaire (€) | Prix total (€) | Image | Caractéristiques | Courbes caractéristiques | Disponibilités 19/04/2023 | Schéma | Lien + Remarques
Débitmètre | Honeywell Zephyr (HAFUHH0200L4AXT) | 1 | 270 € | 270.00 € |  | Supply voltage : 3,3 Vdc Plage de débit : 0 - 200 l/min Résolution : 0,029 l/min Pression max : 60 Psi Communication I2C |  | Farnell : 67 Digikey : 66 RS : 4 |  | https://fr.rs-online.com/web/p/debimetres/2017960
Débitmètre (Alternative) | Sensirion SFM3300-250-D (3ème option : Sensirion SFM3019) | 1 | 43.00 € | 43.00 € |  | Supply voltage : 5V Précision : 5% Résolution : 0,034 l/min Plage de débit : -250 to 250 l/min Pression max : 1,1 bar Intègre une interface de communication |  | Mouser : 2320 Farnell : 22 |  | https://www.mouser.fr/ProductDetail/Sensirion/SFM3300-D?qs=u16ybLDytRa%2FjhQAbeBcMw%3D%3D
Capteur de pression | ABP2MRRT060MD2A3XX | 1 | 30 € | 30.00 € |  | Communication I2C Plage de mesure : -60 à 60 mbar Supply voltage : 3.3V Accuracy : ±0.25% |  | Farnell : 1 Digikey : 472 Mouser : 72 RS : 102 |  | https://fr.rs-online.com/web/p/ci-de-capteur-de-pression/2198129
Capteur de pression (alternative) | MPX5010DP | 1 | 23 € | 23.00 € |  | Sortie analogique Plage de mesure : 0 à 10 kPa Supply voltage : 5V Accuracy : ±5% |  | Farnell : 1119 Mouser : 7817 |  | https://fr.farnell.com/nxp/mpx5010dp/pressure-capteur/dp/1555605?mckv=_dc|pcrid||plid||kword||match||slid||product|1555605|pgrid||ptaid||&CMP=KNC-GFR-GEN-SHOPPING-Hybrid-ePmax-MidScore-17-Jan-23&gross_price=true
Afficheur de données | LCD Displaytech 204A | 1 | 23 € | 23.00 € |  | Supply voltage : 5V Afficheur 20x4 Affichage STN Communication en série |  | RS : 78 Farnell : 455 |  | https://fr.rs-online.com/web/p/afficheurs-monochromes-lcd/5326824?matchtype=&aud-827186183686:pla-317410889898&gclsrc=aw.ds
Afficheur de données (alternative) | Ecran couleur LCD RS PRO | 1 | 15 € | 15.00 € |  | Supply voltage : 3.3V Afficheur 80x160 pixels Affichage TFT Communication I2C |  | RS : En stock |  | https://fr.rs-online.com/web/p/ecrans-tftlcd/1809035?matchtype=&aud-827186183686:pla-301920220064&gclsrc=aw.ds
Blower | Moteur de ventilateur axial Bmc cpap | 1 | 64 € | 64.00 € |  | Signal PPM (Pulse Position Modulation) Tension nominale : 24V Vitesse max : 33000 tr/min Pression : 5000 Pa |  | Aliexpress : En Stock |  | https://fr.aliexpress.com/item/1005005316772932.html?curPageLogUid=ZoeRoCkxBo3N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
Blower (alternative) | WS7040-12/24 | 1 | 68 € | 68.00 € |  | Signal PWM Tension nominale : 24V Vitesse max : 36000 tr/min Pression : 6500 Pa Carte de contrôle intégrée |  | Aliexpress : En Stock |  | https://fr.aliexpress.com/item/32980201709.html?scm_id=1007.40000.326746.0&scm-url=1007.40000.326746.0
Microcontrôleur | Nucleo STM32f411re | 1 | 16 € | 16.00 € |  | Power supply : 1,7V to 3,6V Résolution : 32 bits Mémoire: 128 Kbytes SRAM 512 Kbytes Flash 81 I/O ports Clock: 4 to 26 MHz Communication I2C, SPI, UART,USB 8 Timers |  | Farnell : 75 Mouser : 376 Digi Key : 10 |  | https://os.mbed.com/platforms/ST-Nucleo-F411RE/
Microcontrôleur (alternative) | Arduino Mega 2560 Rev3 | 1 | 42 € | 42.00 € |  | Power supply : 1,7V to 3,6V Input Voltage : 7V to 12V Résolution : 8 bits Mémoire: 8 Kbytes SRAM 256 Kbytes Flash 4 Kbytes EEPROM 70 I/O ports Clock: 16 MHz Communication I2C, SPI, UART 8 Timers |  | Arduino shop : en stock RS : 207 Amazon : en stock GoTronic : en stock |  | https://fr.rs-online.com/web/p/arduino/7154084?matchtype=&aud-827186183886:pla-369227342804&gclsrc=aw.ds
Carte de puissance | Arotelicht LED Alimentation Transformateur 24V 6A | 1 | 23 € | 23.00 € |  | Technologie : AC/DC Entrée : 110 - 240VDC 50Hz Sortie : 144W 24V 6A |  | Amazon : En stock |  | https://www.amazon.fr/dp/B07WMRXRNR?s=electronics&sp_csd=d2lkZ2V0TmFtZT1zcF9kZXRhaWw
Carte de puissance (alternative) | FSKE Alimentation Adaptateur Transformateurs 24V 4A | 1 | 25 € | 25.00 € |  | Technologie : AC/DC Entrée : 100 - 240VDC 50Hz Sortie : 96W 24V 4A |  | Amazon : En stock |  | https://www.amazon.fr/dp/B07CSWRL6F?s=electronics&sp_csd=d2lkZ2V0TmFtZT1zcF9kZXRhaWw
Boutons poussoirs |  |  |  | 0.00 €
Interrupteur On/OFF | Interrupteur à bascule DPST On-Off | 1 | 5 € | 5.00 € |  | Tension max : 250V Courant de contact : 16A Dimension : 30x22 mm |  | RS : 903 |  | https://fr.rs-online.com/web/p/interrupteurs-a-bascule/2789828?matchtype=&aud-827186183686:pla-341677437275&gclsrc=aw.ds
Tuyau PPC |  | 1 | 20 € | 20.00 € |  | Section : 22 mm Longueur : 180 cm |  | CPAP-Store : En Stock |  | https://www.cpap-store.fr/produit/tuyau-ppc-tuyau-de-remplacement-22mm/
Mixer O2 + Filtre | Filtre médical jetable | 1 | 5 € | 5.00 € |  | Section d'entrée : 15 mm Section de sortie : 22 mm |  | Aliexpress : En stock |  | https://fr.aliexpress.com/item/1005003526572069.html
Câbles Elegoo |  | 1 | 10 € | 10.00 € |  | 120 câbles |  |  |  | https://www.amazon.fr/Elegoo-Breadboard-Femelle-Longueur-Arduino/dp/B01JD5WCG2
Câble débitmètre |  | 1 | 3 € | 3.00 € |  | 6 broches |  |  |  | https://fr.rs-online.com/web/p/cordons-fil-a-carte/1862826?matchtype=&aud-827186183686:pla-302974859937&gclsrc=aw.ds
Masque nasal | "Autre choix possible" | 1 | 26 € | 26.00 € |  |  |  |  |  | https://fr.aliexpress.com/item/1005001604530552.html?scm_id=1007.40000.327270.0&scm-url=1007.40000.327270.0&ad_pvid=202303090922547024111610671195187406_4
Bobines PLA 1 kg | "Autre choix possible" | 2 | 24 € | 48.00 € |  | Diamètre : 1.75 mm |  |  |  | https://www.amazon.de/Amazon-Basics-Printer-Filament-1-75mm/dp/B08895V44X?adgrpid=85042010154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
Tuyau 15 mm |  | 1 | 14 € | 14.00 € |  | Diamètre : 15x20 mm |  |  |  | https://www.amazon.fr/Silicone-Flexible-%C3%A9paisseur-Tuyau-m%C3%A8tre/dp/B09V73GYYZ?adgrpid=59831306127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
Partie test du système
Poumon artificiel |  | 1 | 77 € | 77.00 € |  |  |  |  |  | https://fr.aliexpress.com/item/32813287274.html
 |  | Min | Max
Système complet | Prix total : | 315.00 € | 589.00 €
Système sur le marché (CPAP-Store) | Référence prix : | 500 € | 1200 €

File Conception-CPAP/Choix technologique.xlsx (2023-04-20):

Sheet: Systeme
Fonction | Solution trouvée | Technologie | Avantage | Inconvénient | Caractéristiques | Prix | Choix | Remarques
Configurer la quantité d'air envoyée par l'appareil | Boutons | Boutons poussoirs | Simple d'utilisation Facile à intégrer Très peu cher |  |  | 0,5 € | X
Transmettre l'air au patient | Connecteurs pneumatique + Masque facial (nez et bouche) | Impression 3D | Facilement modulable Pas cher Très accessible |  |  |  | X |  | https://fr.aliexpress.com/item/4000205864783.html?_t=pvid%3A7e358efb-93cc-4054-aae8-19941c556692 https://www.fruugo.fr/masque-facial-cpap-stop-snoring-nm2-nm4-masque-nasal-pour-masque-sleep-snore-cpap-respirateur-sangle/p-97020003-204255127?language=fr | https://fr.aliexpress.com/item/4000320348721.html?_t=pvid%3A43b0de8a-f24d-44cd-a72a-0154e2d15bb8
Mesurer la quantité d'air envoyée | Débitmètre | FS1012-1100-NG | Plage de mesure suffissante Facile à intégrer et à prototyper Pas trop cher | Moins précis | Range : 0 à 10 SLM Supply voltage: 3V to 5V Communication SPI | 45 €
 |  | Sensirion | Précis et Fiable Grande plage de mesure Facile à intégrer Homologué pour le médical |  | Range : -10 to 240slm Accuracy : ±2% Resolution : 16 bit Supply Voltage : 3,3V Communication I2C | 170 €
 |  | Honeywell Zephyr (200 SLM) | Précis et Fiable Grande plage de mesure Facile à intégrer Homologué pour le médical | Prix très élevé | Range : 0 to 200 slm Pipe Diameter Range 15mm Supply Voltage : 3 à 10V Resolution : 0.029 SLPM Accuracy : 3,5% (reading) | 243 € | X | Débitmètre en stock
 | Capteur de pression différentiel | Sensirion SDP8 ou SEN0343 (prototypage avec Arduino) | Très fiable Très stable Précis Plage de mesure suffissante | Assez encombrant Communication I2C | Supply voltage : 3,3V Range : -500 to + 500 Pa Communication I2C Accuracy : 0,1 Pa Répétitivité : 0,05 Pa | 36€ ou 44€ |  | Capteur de pression différentiel car très commun dans le médical
 |  | Honeywell APB2 series ABP2DDAN005NDAA5XX | Fiable Précis Plage de mesure suffissante boîtier SIP |  | Range : ± 1 kPa Supply Voltage ; 3,3V Sortie Analogique | 42 € |  |  | https://fr.rs-online.com/web/p/ci-de-capteur-de-pression/2269027
 |  | MPXV7002DP | Fiable Stable Précis Plage de mesure suffissante | boîtier SOIC | Supply Voltage : 5V Accuracy : ± 2,5% Range : ± 2kPa Sortie Analogique | 32 € |  |  | https://fr.farnell.com/nxp/mpxv7002dp/capteur-pressure-double-diff-0/dp/2080499
 |  | MPX5010DP | Fiable Stable Précis boîtier SIP | Plage de mesure positive | Supply Voltage 5V Accuracy : 5% Range : 0 à 10 kPa Sortie Analogique | 33 € |  |  | https://fr.farnell.com/nxp/mpx5010dp/pressure-capteur/dp/1555605
 |  | Sensirion SDP1000 | Fiable Précis boîtier PPS Sortie analogique | prix élevé | Supply Voltage : 5V Accuracy : ± 1,5% Range : -20 à 500Pa Sortie Analogique (0 ,25 à 4V) | 89 € |  |  | https://fr.rs-online.com/web/p/capteurs-de-pression/1732220
 |  | ABP2MRRT060MD2A3XX | Fiable Stable Précis boîtier SMD-6 Sortie 3,3V Plage de mesure de suffisante | Communication I2C | Supply Voltage : 3,3V Accuracy : ± 0.25 % Range : -60 à 60 mbar Communication I2C | 28 € | X |  | https://www.mouser.fr/ProductDetail/Honeywell/ABP2MRRT060MD2A3XX?qs=pUKx8fyJudCPHkZ6wdjrNg%3D%3D
Récupérer l'air externe | Pompe à air | Micronel U series | Fiable Simple d'utilisation Peu encombrant Range suffissante | Bruyante Peu accessible | Brushless DC Motor Supply voltage : 24V Range : 0 à 500 l/min Pressure : 54 hPa Noise : 42 ou 66 dB Intégre un Tachomètre 4 fils de connexion | Sous devis |  | Range nécessaire : 20 à 60 l·min-1
 |  | Boreasa C60S1 | Fiable Simple d'utilisation Peu encombrant Range suffissante | Pas d'information sur le bruit Peu accessible | Brushless DC Motor Supply voltage : 24V Range : 0 à 230 l/min Pressure : 34 hPa Intégre un Capteur à effet Hall 3 fils de connexion | Sous devis
 |  | Blower MakAir | Fiable Déjà intégré et en stock Range suffissante Peu encombrant | Peu d'information | Brushless DC Motor Supply voltage : 24V Range : 0 à 300 l/min Pressure : 34 hPa Noise : 40 dB Intégre un Capteur à effet Hall 6 fils de connexion | En stock | X | Moins adapté mais en stock
 |  | Ventilateur centrifuge RS PRO | Fiable Facilement intégrable Peu cher Suffissant pour du prototypage | Pas dans les normes médicales | Airflow : 120 l/min Supply voltage : 12V Noise : 38dB 12,8 mmH2O | 18 €
 |  | Ventilateur centrifuge RV40 | Fiable Facilement intégrable Suffissant pour du prototypage | Cher | Airflow : 400 l/min Supply voltage : 12V Noise : 50dB 24m³/h Commande PWM | 90 € |  | Plus adapté mais pas en stock
 |  | Blower San Ace B97 | Fiable Facilement intégrable Suffissant pour du prototypage Plusieurs gammes |  | Airflow : 0,125 to 1,85 m3/min Static pressure : 121 to 1950 Pa Supply Voltage : 12 ou 24 V Noise : 44 ou 69 dB Commande PWM Pulse sensor intégré | 66 €
 |  | BFN0724SS-0/BFN0724 | Facilement intégrable Caractéristiques adaptées Pas cher Silencieux | aliexpress | Airflow : 511 l/min Static pressure : 50 cmH2O Supply voltage : 24V Noise : 38dB(A) Commande PWM Speed : 31500 RPM | 45 € |  |  | https://fr.aliexpress.com/item/1005004095080981.html?scm_id=1007.13339.291025.0&scm-url=1007.13339.291025.0 https://fr.aliexpress.com/item/1005004095141705.html?scm_id=1007.13339.291025.0&scm-url=1007.13339.291025.0
 |  | Moteur de ventilateur axial Bmc cpap | Facilement intégrable Caractéristiques adaptées Pas cher Silencieux | aliexpress | Airflow : 2000 cfm Haute pression Supply voltage : 24V Noise : 16dB(A) Commande PWM | 66 € |  |  | https://fr.aliexpress.com/item/1005004604155490.html?scm_id=1007.40050.281175.0&scm-url=1007.40050.281175.0
 |  | Souffleur centrifuge WS7040 | Facilement intégrable Caractéristiques adaptées Pas cher Silencieux | aliexpress Pilote fournit obligatoire | Airflow : 260 l/min Static pressure : 5,5 kPa Supply voltage : 12V/24V Noise : 45dB(A) Commande PWM Speed : 35000 RPM Intégre un capteur Hall | 58 € |  |  | https://fr.aliexpress.com/item/1005004431141160.html?curPageLogUid=zzkvoDFUl3DA
Apporter de l'air "propre" | Filtre | filtre coton (commun pour les filtres CPAP) | Très accessible Pas cher Efficace | Moins écologique |  | 1 € | X
 |  | filtre PET recyclé | Pas cher Efficace Plus écologique | Moins accessible Moins commun dans le médical |  | 2,6€
Afficher les données de l'appareil en temps réel | Ecran | Waveshare 2inch LCD Display | Fiable Simple d'utilisation Pas cher Facilement intégrable |  | Taille : 2 inch Communication I2C | 17 €
 |  | QAPASS LCD 16x2 ou Displaytech 204A | Simple d'utilisation Facilement intégrable Pas cher | Peu de caractère à afficher (Qapass) | Taille : 16x2 caractères Communication I2C ou Taille : 20 x4 caractères Supply voltage : 3,3V ou 5V 16 broches | Gratuit (en stock) | X
 |  | AZDelivery Écran ST7735 | Facilement intégrable Intègre TFT Assez grand écran |  | Taille : 1,77 pouces Communication I2C | 11,49€ |  | Plus adapté mais pas en stock
Enregistrer les données pour le médecin traitant | SD | GT126 | Adapté au prototypage Simple d'intégration Accessible et disponible |  | Communication SPI Supply Voltage : 3,3V ou 5V | 2,2€
 |  | Sparkfun BOB-00544 | Simple d'intégration Accessible et disponible | Soudure à faire | Communication SPI Supply Voltage : 3,3V ou 5V | 5,73€
Alimenter l'appareil | Transformateur + (Rechargement des batteries) | PCS – 100B | En stock Facilement intégrable Meilleure gestion d'énergie | Encombrant Tension de sortie élevée | Technologie: AC/DC Entrée: - 127 - 370VDC - 47 – 63Hz - 2A/115VAC et 1.2A/230VAC Sortie: - 100W - 27,6V - 3,5A Rendement: 86% | En stock | X | Plus cher et moins adapté mais en stock
 |  | LRS-100 series | Facilement intégrable Meilleure gestion d'énergie Tension de sortie suffissante | Encombrant | Entrée : 85 - 264V AC Sortie : 5 ou 12 V Fréquence : 47 - 63 Hz Rendement: 86% | 21 € |  | Moins cher et plus adapté mais pas en stock
 | Batteries (Si PCS - 100B choisi) | YUASA NP7-12 |  |  | Technologie: Plomb-calcium Capacité: 12V/7Ah Perte : 3% en capacité par mois (20°C) | 40 € |  | Le système n'a pas besoin de batteries car le patient ne sera pas en danger en cas de coupure de courant
 |  | AGM 12V - 7Ah |  |  | Technologie: Plomb-étanche Capacité: 12V/7Ah | 24 €

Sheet: Capteur_pression
Solution trouvée | Technologie | Avantage | Inconvénient | Caractéristiques | Prix | Choix | Lien
Capteur de pression différentiel | Sensirion SDP8 ou SEN0343 (prototypage avec Arduino) | Très fiable Très stable Précis Plage de mesure suffissante | Assez encombrant Communication I2C | Supply voltage : 3,3V Range : -500 to + 500 Pa Communication I2C Accuracy : 0,1 Pa Répétitivité : 0,05 Pa | 36€ ou 44€
 | Honeywell APB2 series ABP2DDAN005NDAA5XX | Fiable Précis Plage de mesure suffissante boîtier SIP |  | Range : ± 1 kPa Supply Voltage ; 3,3V Sortie Analogique | 42 € |  | https://fr.rs-online.com/web/p/ci-de-capteur-de-pression/2269027
 | MPXV7002DP | Fiable Stable Précis Plage de mesure suffissante | boîtier SOIC | Supply Voltage : 5V Accuracy : ± 2,5% Range : ± 2kPa Sortie Analogique | 32 € |  | https://fr.farnell.com/nxp/mpxv7002dp/capteur-pressure-double-diff-0/dp/2080499
 | MPX5010DP | Fiable Stable Précis boîtier SIP | Plage de mesure positive | Supply Voltage 5V Accuracy : 5% Range : 0 à 10 kPa Sortie Analogique | 33 € |  | https://fr.farnell.com/nxp/mpx5010dp/pressure-capteur/dp/1555605
 | Sensirion SDP1000 | Fiable Précis boîtier PPS Sortie analogique | prix élevé | Supply Voltage : 5V Accuracy : ± 1,5% Range : -20 à 500Pa Sortie Analogique (0 ,25 à 4V) | 89 € |  | https://fr.rs-online.com/web/p/capteurs-de-pression/1732220
 | ABP2MRRT060MD2A3XX | Fiable Stable Précis boîtier SMD-6 Sortie 3,3V Plage de mesure de suffisante | Communication I2C | Supply Voltage : 3,3V Accuracy : ± 0.25 % Range : -60 à 60 mbar 204 Samples/s Communication I2C | 28 € | X | https://www.mouser.fr/ProductDetail/Honeywell/ABP2MRRT060MD2A3XX?qs=pUKx8fyJudCPHkZ6wdjrNg%3D%3D

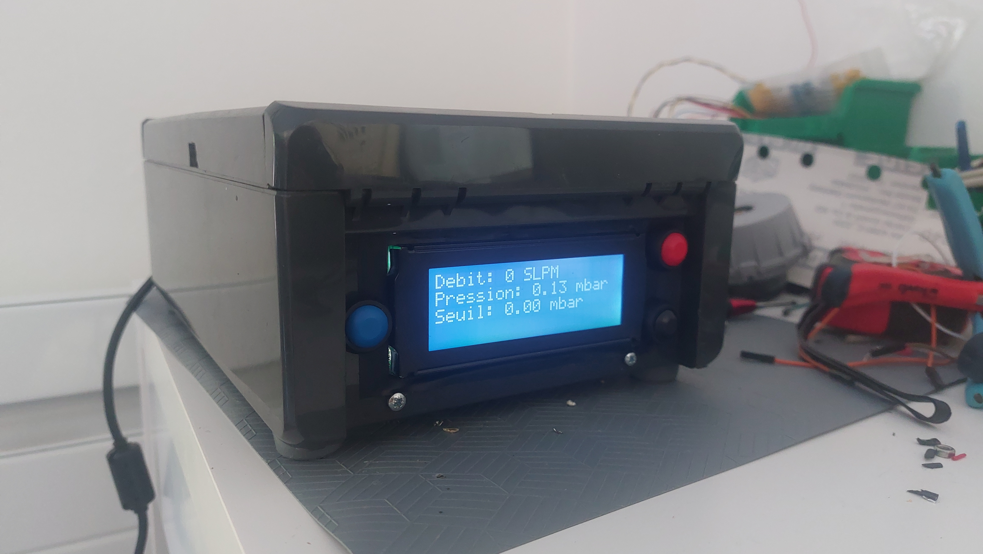
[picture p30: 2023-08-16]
Parts-CPAP/Case_V2/IHM.jpg

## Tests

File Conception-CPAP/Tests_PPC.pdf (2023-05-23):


# BOUTRY Loan

# Alternant sur le projet MakAir


# Tests du respirateur PPC

Ce document fait partie d’une série de livrables concernant la conception et le prototypage

# d’un respirateur à pression positive continue pour diminuer l’apnée du sommeil d’un patient

# Ce livrable a pour but d’énoncer et d’expliquer les tests qui vont être réalisés sur les différents composants du système. Les résultats seront aussi analysés au fur à mesure de l’avancement de la réalisation

# Table des matières

Table des figures | 3
Blower | 4
Test n°1 : Envoi d’air avec une vitesse fixe | 4
Objectif : | 4
Contexte : | 4
Réalisation : | 4
Résultats : | 4
Test n°2 : Envoi d’air avec une vitesse variable | 5
Objectif : | 5
Contexte : | 5
Réalisation : | 5
Résultats : | 5
Débitmètre | 6
Test n°3 : Mesurer un débit d’air variable | 6
Objectif : | 6
Contexte : | 6
Réalisation : | 6
Résultats : | 6
Capteur de pression | 7
Test n°4 : Mesurer une pression d’air variable | 7
Objectif : | 7
Contexte : | 7
Réalisation : | 7
Résultats : | 7
IHM | 8
Test n°5 : Afficher le débit d’air et la pression d’air | 8
Objectif : | 8
Contexte : | 8
Réalisation : | 8
Résultats : | 8
Test n°6 : Configurer des données du système | 9
Objectif : | 9
Contexte : | 9
Réalisation : | 9
Résultats : | 9
Respirateur PPC (intégration) | 10
Test n°7 : Commander la vitesse | 10
Objectif : | 10
Contexte : | 10
Réalisation : | 10
Résultats : | 11
Test n°8 : Commander le débit d’air | 12
Objectif : | 12
Contexte : | 12
Réalisation : | 12
Résultats : | 13
Test n°9 : Commander la pression de l’air | 14
Objectif : | 14
Contexte : | 14
Réalisation : | 14
Résultats : | 15
Test n°10 : Piloter le respirateur PPC | 16
Objectif : | 16
Contexte : | 16
Réalisation : | 16
Résultats : | 17

# Table des figures

# Figure 1 : Test n°1 | 4 Figure 2 : Test n°2 | 5 Figure 3 : Test n°3 | 6 Figure 4 : Test n°4 | 7 Figure 5 : Test n°5 | 8 Figure 6 : Test n°6 | 9 Figure 7 : Test n°7 | 10 Figure 8 : Test n°8 | 12 Figure 9 : Test n°9 | 14 Figure 10 : Test n°10 | 16

# Blower

# Test n°1 : Envoi d’air avec une vitesse fixe

# Objectif :

# - Observer le fonctionnement du blower - Valider l’envoi d’air externe par le blower

# Contexte :

# - Seulement la carte de contrôle est branchée au microcontrôleur sur la broche D10 - Alimentation 12V câblée à la carte de contrôle

# Réalisation :

# - Envoi d’un signal PPM de 50 Hz par le microcontrôleur à la carte de contrôle - Vitesse fixe à 50% pendant 1 min

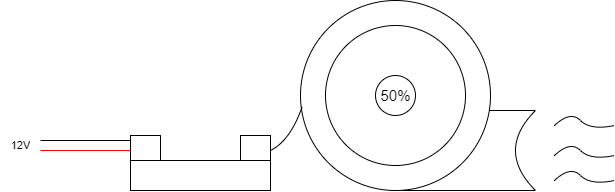
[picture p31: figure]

# Figure 1 : Test n°1

# Résultats :

Essai | Validation ? | Observations
1 ❌ | | - Le moteur émet un son mais n’envoie pas d’air - Problème sur le signal émis : c’est un signal PWM et non un signal PPM
2 ✅ | | - Le blower envoie de l’air en continu - Le blower correspond à la consigne (1 min) - Le blower a une pression peu importante, sûrement dû à la tension d’alimentation

# Test n°2 : Envoi d’air avec une vitesse variable

# Objectif :

# - Observer le fonctionnement du blower avec une variation de vitesse - Valider la variation d’air envoyé par le blower - Trouver la meilleure solution pour l’alimentation du blower

# Contexte :

# - Seule la carte de contrôle est branchée au microcontrôleur sur la broche D10 - Alimentation 12V (1er essai) ou 24V (2ème essai) câblée à la carte de contrôle

# Réalisation :

# - Envoi d’un signal PPM de 50 Hz par le microcontrôleur à la carte de contrôle - Vitesse variant de 0% à 100% pendant 1 min - Changement de l’alimentation entre chaque essai

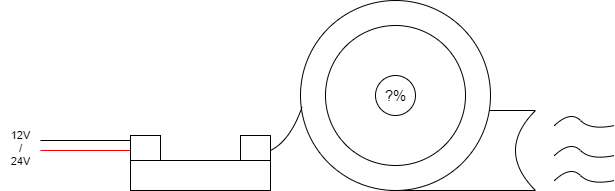
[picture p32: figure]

# Figure 2 : Test n°2

# Résultats :

Essai | Validation ? | Observations
1 ✅ | | - Le moteur varie sa vitesse de 0 à 100% - Le moteur est à l’arrêt à 0% et n’est pas au maximum à 100% par rapport à ses caractéristiques - L’alimentation doit passer à 24V pour avoir des caractéristiques répondant au cahier des charges
2 ✅ | | - Le moteur varie sa vitesse de 0 à 100% - Le moteur est à l’arrêt à 0% et est au maximum à 100% - L’alimentation 24V est donc la meilleure solution pour répondre au cahier des charges

# Débitmètre

# Test n°3 : Mesurer un débit d’air variable

# Objectif :

# - Observer le fonctionnement du débitmètre - Valider la communication I2C entre le capteur et le microcontrôleur - Récupérer le débit d’air envoyé par une source d’air (Souffle d’un humain ou ventilateur)

# Contexte :

# - Seulement le débitmètre est branché au microcontrôleur sur la broche D14 et D15 - Source d’air sous pression indépendante du système

# Réalisation :

# - Communication I2C entre le capteur et le microcontrôleur - Varier le débit d’air envoyée avec une intervalle d’au moins 30 SLPM

# Figure 3 : Test n°3

# Résultats :

Essai | Validation ? | Observations
1 ❌ | | - Le débitmètre ne renvoie aucune valeur. - L’initialisation de la communication I2C semble poser des problèmes
2 ❌ | | - Le numéro de série I2C du capteur est reçu donc l’initialisation est validée - Aucune donnée n’est reçue par le capteur malgré une communication I2C établie. Le problème semble matériel
3 ✅ | | - Le problème venait des résistances branchées sur les signaux SDA et SCL. Suite au changement, les données du débit d’air sont reçues par le système. - Une variation du débit d’air entre 20 et 70 SLPM est reçue. Le fonctionnement du débitmètre est validé

# Capteur de pression

# Test n°4 : Mesurer une pression d’air variable

# Objectif :

# - Observer le fonctionnement du capteur de pression - Valider la communication I2C entre le capteur et le microcontrôleur

- Récupérer la pression de l’air par une source d’air (Souffle d’un humain ou ventilateur)

# Contexte :

# - Seulement le capteur de pression est branché au microcontrôleur sur la broche D3 et

D6

# - Source d’air sous pression indépendante du système

# Réalisation :

# - Communication I2C entre le capteur et le microcontrôleur - Varier la pression de l’air envoyée avec une intervalle d’au moins 5 mbar

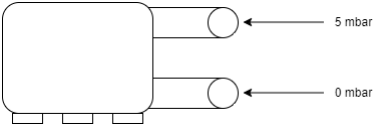
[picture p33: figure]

# Figure 4 : Test n°4

# Résultats :

Essai | Validation ? | Observations
1 ❌ | | - Le capteur de pression ne renvoie aucune valeur. - Le capteur ne semble pas être fonctionnel, cela doit être un problème au niveau du câblage
2 ✅ | | - Le capteur envoie des données, le problème venait de la soudure d’une des broches qui était cassée - Une variation de 5 mbar est captée. Cela valide le fonctionnement du capteur

# IHM

# Test n°5 : Afficher le débit d’air et la pression d’air

# Objectif :

# - Observer le fonctionnement de l’afficheur - Valider l’affichage de données captées par les capteurs

# Contexte :

# - Connecter l’afficheur et le débitmètre au premier essai et ensuite le capteur de pression au deuxième essai - Source d’air sous pression indépendante du système

# Réalisation :

# - Varier le débit d’air et la pression de l’air - Afficher les données reçues par le microcontrôleur

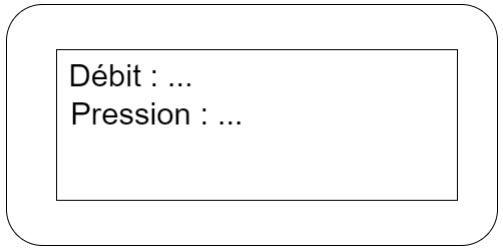
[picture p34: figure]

# Figure 5 : Test n°5

# Résultats :

Essai | Validation ? | Observations
1 | ✅ | L’afficheur affiche le débit d’air qui varie en fonction de la source d’air
2 | ✅ | L’afficheur affiche la pression de l’air qui varie en fonction de la source d’air

# Test n°6 : Configurer des données du système

# Objectif :

# - Observer le fonctionnement de l’IHM - Valider l’IHM

# Contexte :

# - Connecter l’afficheur et les boutons

# Réalisation :

# - Simuler la configuration de la vitesse du blower - Afficher les données configurées

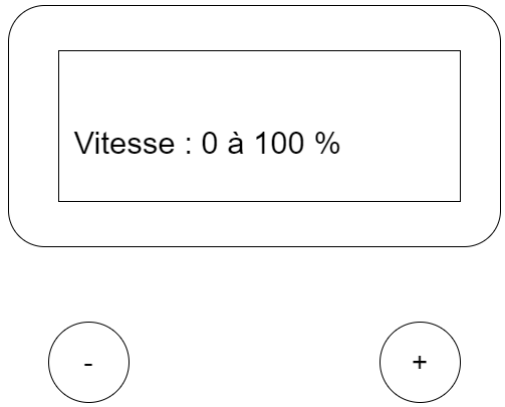
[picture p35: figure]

# Figure 6 : Test n°6

# Résultats :

Essai | Validation ? | Observations
1 ✅ | | - L’afficheur affiche la vitesse qui est configuré par les boutons - La configuration modifie la vitesse en la diminuant (bouton -) ou en l’augmentant (bouton +)

# Respirateur PPC (intégration)

# Test n°7 : Commander la vitesse

# Objectif :

# - Valider l’intégration de chaque composant - Observer le fonctionnement du système en modifiant un des paramètres (vitesse)

# Contexte :

# - Connecter tous les composants du système - Alimentation 24V sur la carte de contrôle du blower - Alimentation 5V par l’USB d’un ordinateur

# Réalisation :

# - Configurer la vitesse du blower avec l’IHM - Contrôler la vitesse du blower - Récupérer le débit d’air et la pression - Afficher les données du système

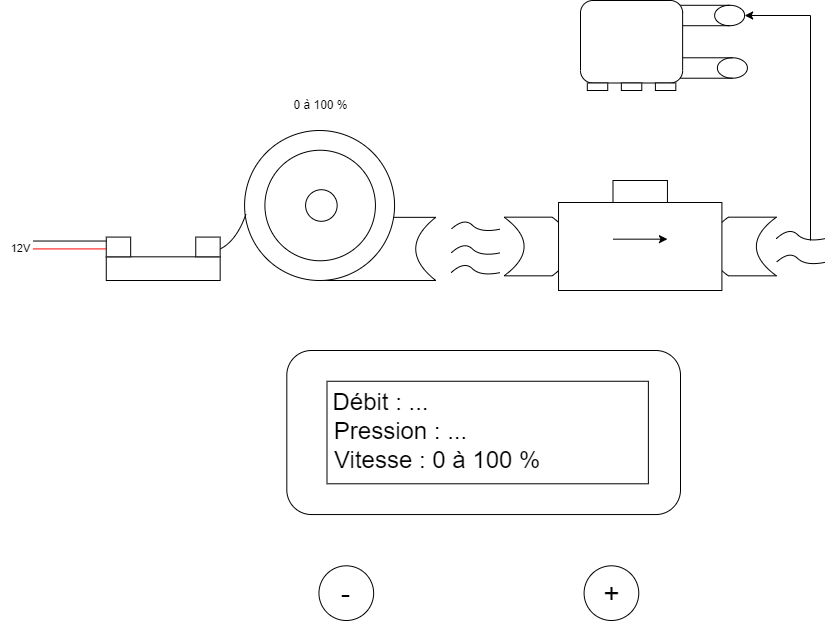
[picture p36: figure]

# Figure 7 : Test n°7

# Résultats :

Essai | Validation ? | Observations
1 ❌ | | - La configuration de la vitesse se passe sans problème - Seulement le débit d’air est renvoyé, la pression n’est pas renvoyée par le capteur - Le problème vient de la communication I2C qui se fait seulement avec le débitmètre
2 ✅ | | - Suite à l’utilisation de « TwoWire », la pression est maintenant renvoyée par le capteur - La commande de la vitesse du blower et l’intégration des composants sont validées

# Test n°8 : Commander le débit d’air

# Objectif :

# - Valider l’intégration de chaque composant - Valider la boucle de régulation en débit - Observer le fonctionnement du système en modifiant un des paramètres (débit d’air)

# Contexte :

# - Connecter tous les composants du système - Alimentation 24V sur la carte de contrôle du blower - Alimentation 5V par l’USB d’un ordinateur

# Réalisation :

# - Configurer le débit d’air souhaité avec l’IHM - Contrôler la vitesse du blower en fonction du débit d’air - Récupérer le débit d’air et la pression - Afficher les données du système

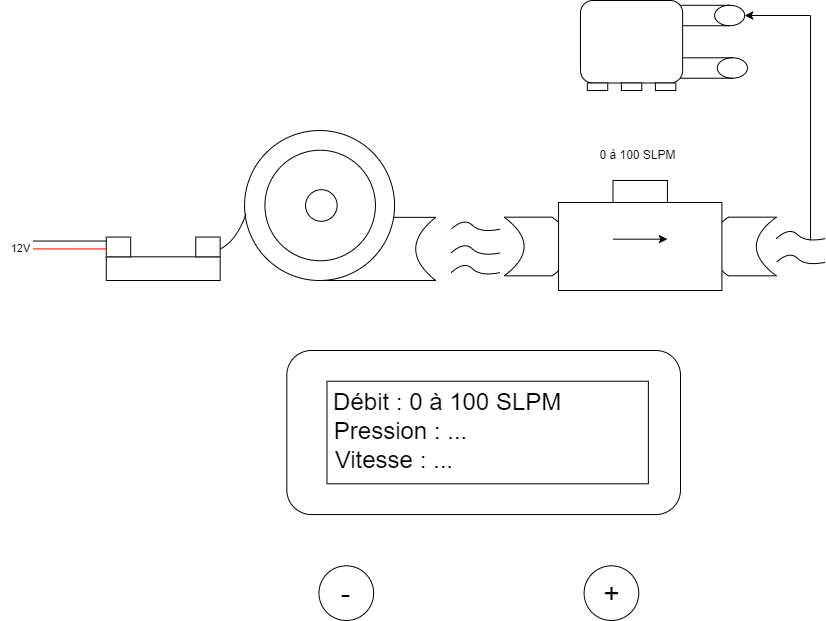
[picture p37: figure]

# Figure 8 : Test n°8

# Résultats :

Essai | Validation ? | Observations
1 ❌ | | - La configuration du débit d’air fonctionne mais le blower augmente sa vitesse à l’infini jusqu’à sa limite - Le système est dans une boucle infinie lorsqu’il veut atteindre le seuil configuré
2 ✅ | | - Le problème logiciel est réglé - Le système peut être commandé en débit d’air. Le test est donc validé

# Test n°9 : Commander la pression de l’air

# Objectif :

# - Valider l’intégration de chaque composant - Valider la boucle de régulation en pression - Observer le fonctionnement du système en modifiant un des paramètres (pression)

# Contexte :

# - Connecter tous les composants du système - Alimentation 24V sur la carte de contrôle du blower - Alimentation 5V par l’USB d’un ordinateur

# Réalisation :

# - Configurer la pression d’air souhaitée avec l’IHM - Contrôler la vitesse du blower en fonction de la pression - Récupérer le débit d’air et la pression - Afficher les données du système

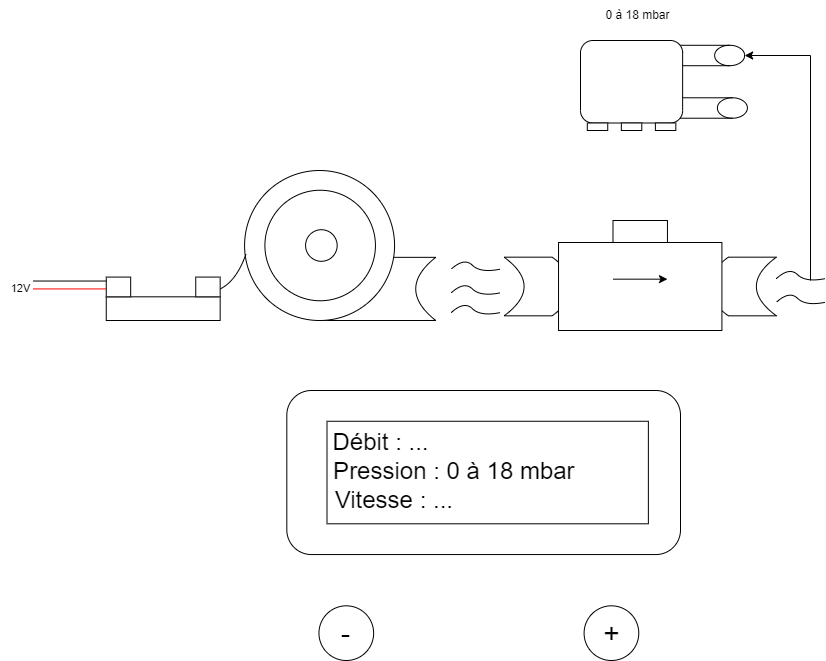
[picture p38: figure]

# Figure 9 : Test n°9

# Résultats :

Essai | Validation ? | Observations
1 ✅ | | - Le système peut être commandé en pression. Le test est donc validé

# Test n°10 : Piloter le respirateur PPC

# Objectif :

# - Valider l’intégration de chaque composant - Observer le fonctionnement du système complet

# Contexte :

# - Connecter tous les composants du système - Alimentation 24V sur la carte de contrôle du blower - Alimentation 5V par l’USB d’un ordinateur

# Réalisation :

# - Configurer les seuils de pression du respirateur PPC - Contrôler la vitesse du blower en fonction des seuils - Récupérer le débit d’air et la pression - Afficher les données du système

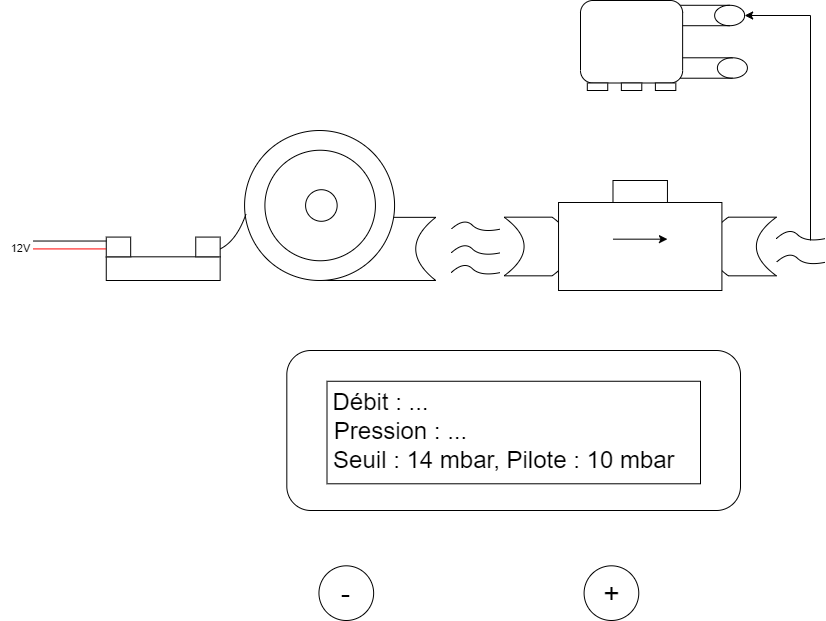
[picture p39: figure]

# Figure 10 : Test n°10

# Résultats :

Essai | Validation ? | Observations
1 ❌ | | - La configuration des seuils se passe sans problème - Le système est dans une boucle infinie lorsqu’il veut atteindre le deuxième seuil configuré
2 ❌ | | - Le système fonctionne mais la simulation de respiration avec le poumon artificiel n’est pas valide car le système ne répond pas au cahier des charges - Le système ne réagit pas comme un respirateur PPC autopiloté

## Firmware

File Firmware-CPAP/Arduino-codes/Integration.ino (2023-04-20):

#define ESC_PPM_PERIOD 20000 // 50Hz
#define AIRFLOW_PERIOD 100000 // 10Hz
#define PRESSURE_PERIOD 200000 // 5Hz
#define MIN_BLOWER_SPEED 300u
#define MAX_BLOWER_SPEED 1800u
#define DEFAULT_BLOWER_SPEED 900u
#define PIN_ESC_BLOWER  PB6  // D10 / TIM4_CH1
#define TIM_CHANNEL_ESC_BLOWER 1 //Channel 1 de la pin D10
#define TIM_CHANNEL_AIRFLOW 4 //Channel 4 de la pin D15
#define TIM_CHANNEL_PRESSURE 2 //Channel 2 de la pin D3
#define BlowerSpeed2MicroSeconds(value) map(value, 0, 1800, 1000, 1950) //Intervalle [1ms à 1,95 ms] sur la variation de vitesse du blower, on élargit cette intervalle pour avoir une plus grande plage de commande du Blower
#define MFM_HONEYWELL_HAF_I2C_ADDRESS 0x49 //Adresse du debitmetre
#define PIN_I2C_SDA PB9 //I2C1
#define PIN_I2C_SCL PB8 //I2C1
#define PRESSURE_SDA PB3 //I2C2
#define PRESSURE_SCL PB10 //I2C2

#include <Wire.h>
#include "HardwareTimer.h"
#include <LiquidCrystal.h>

HardwareTimer* hardwareTimer1;  // Timer Blower command
HardwareTimer* hardwareTimer2;  // Timer Debitmetre command
HardwareTimer* hardwareTimer3;  // Timer Pressure command

LiquidCrystal lcd(PA10, PB4, PA9, PC7, PA7, PA6); //Attribution de l'Afficheur

//Communication I2C multi-slaves
TwoWire myWire1(PIN_I2C_SDA, PIN_I2C_SCL); 
TwoWire myWire2(PRESSURE_SDA, PRESSURE_SCL);

////Variables Blower////
static int speedBlower = MAX_BLOWER_SPEED;

////Variables Débitmètre////
int32_t mfmInspiratoryLastValue = 0; //données brutes du débit d'air
int32_t mfmInspiratoryAirFlow = 0; //données du débit d'air
union {
  uint16_t i;
  int16_t si;
  unsigned char c[2];
} mfmLastData;

////Variables Pressure////
uint8_t id = 0x28; // Adresse I2C du capteur de pression
uint8_t data[7]; // Données en sortie
uint8_t cmd[3] = {0xAA, 0x00, 0x00}; // La commande envoyée au capteur
double press_counts = 0; // Données brutes de la pression
double temp_counts = 0; // Données brutes de la température
double pressure = 0; // Données de la pression
double temperature = 0; // Données de la température
double outputmax = 15099494; // Plage des données de la pression (max)
double outputmin = 1677722; // Plage des données de la pression (min)
double pmax = 60; // Plage de mesure de la pression (max)
double pmin = -60; // Plage de mesure de la pression (min)
double percentage = 0; // Pourcentage de la pression mesurée en fonction de la plage de mesure
char printBuffer[200], cBuff[20], percBuff[20], pBuff[20], tBuff[20];


void setup() {
  Serial.begin(115200);
  myWire1.begin(); //Initialisation de la communication I2C avec le débitmètre
  myWire2.begin();//Initialisation de la communication I2C avec le capteur de pression
  lcd.begin(20, 4); //Initialisation de l'afficheur LCD
  sensor_Init();
  PWM_Blower();
  Airflow_Timer();
  Pressure_Timer();
}

void loop() {

}

void airFlow() { // Cette fonction va permettre de lire le débit d'air mesuré par le débitmètre, elle va être activée dans un timer configuré
  myWire1.begin();
  uint8_t readCount = myWire1.requestFrom(MFM_HONEYWELL_HAF_I2C_ADDRESS, 2); 
  mfmLastData.c[0] = myWire1.read(); //Lecture des données
  mfmLastData.c[1] = myWire1.read();
  myWire1.end();

  mfmInspiratoryLastValue = (uint32_t)(mfmLastData.c[1] & 0xFFu); // masquage 0b00000000000000000000000011111111 & données du registre 1 (falcutatif)
  mfmInspiratoryLastValue |= (((uint32_t)mfmLastData.c[0]) << 8) & 0x0000FF00u; // masquage 0b00000000000000001111111100000000 & données du registre 0 (falcutatif)

  // Unité des données récupérées : Standard Litre Par Minute
  mfmInspiratoryAirFlow = 200 * (((uint32_t)mfmInspiratoryLastValue / 16384.0) - 0.1) / 0.8;

  // Autre formule : Unité des données récupérées : mSLPM
  //mfmInspiratoryAirFlow = (((10 * mfmInspiratoryLastValue) - 16384) * 1526);
  Serial.print("debit d'air : "); 
  Serial.print(mfmInspiratoryAirFlow);
  Serial.println(" SLPM");
  lcd.setCursor(0, 0); //affichage du débit sur le LCD 
  lcd.print("Airflow : ");
  lcd.print(mfmInspiratoryAirFlow);
  lcd.print(" SLPM");
}
void sensor_Init() { // Cette fonction va permettre de lire le numéro de série du débitmètre, elle va être activée une seule fois dans setup()

  myWire1.begin();
  myWire1.beginTransmission(MFM_HONEYWELL_HAF_I2C_ADDRESS);
  myWire1.write(0x02);  // Reset
  uint8_t txOk = myWire1.endTransmission();
  myWire1.end();
  delay(30);

  uint32_t sn = 0;
  myWire1.begin();
  myWire1.beginTransmission(MFM_HONEYWELL_HAF_I2C_ADDRESS);
  uint8_t rxcount = myWire1.requestFrom(MFM_HONEYWELL_HAF_I2C_ADDRESS, 2); // Lire les 2 octets de données du capteur
  sn = myWire1.read();
  sn <<= 8;
  sn |= myWire1.read();  // Première transmission du numéro de série register 0
  sn <<= 8;
  delay(2);  // delay obligatoire pour recevoir le register 1
  rxcount += myWire1.requestFrom(MFM_HONEYWELL_HAF_I2C_ADDRESS, 2);
  sn |= myWire1.read();
  sn <<= 8;
  sn |= myWire1.read();  // Seconde transmission du numéro de série register 1
  Serial.print("Numéro de série : "); 
  Serial.println(sn);
  myWire1.end();
}

void Pressure() { // Cette fonction va permettre de lire la pression mesurée par le capteur de pression, elle va être activée dans un timer configuré
  myWire2.beginTransmission(id);
  int stat = myWire2.write (cmd, 3); // Ecriture pour commander le capteur
  stat |= myWire2.endTransmission();
  delay(10);
  myWire2.requestFrom(id, 7); // Lire les 7 octets de données du capteur
  int i = 0;
  for (i = 0; i < 7; i++) {
    data [i] = myWire2.read();
  }
  press_counts = data[3] + data[2] * 256 + data[1] * 65536; // Calculer les données brutes de la pression
  temp_counts = data[6] + data[5] * 256 + data[4] * 65536; // Calculer les données brutes de la température
  temperature = (temp_counts * 200 / 16777215) - 50; // Calculer la température en °C
  percentage = (press_counts / 16777215) * 100; // Calculer le pourcentage de la pression mesurée en fonction de la plage de mesure
  pressure = ((press_counts - outputmin) * (pmax - pmin)) / (outputmax - outputmin) + pmin;  // Formule pour calculer la pression, trouvable sur la datasheet du capteur
  dtostrf(press_counts, 4, 1, cBuff); 
  dtostrf(percentage, 4, 3, percBuff);
  dtostrf(pressure, 4, 3, pBuff);
  dtostrf(temperature, 4, 3, tBuff);

  sprintf(printBuffer, " % x\t % 2x % 2x % 2x\t % s\t % s\t % s\t % s \n", data[0], data[1], data[2], data[3], cBuff, percBuff, pBuff, tBuff); //Structuration des données dans un Serial
  Serial.print(pBuff);//affichage de la pression
  Serial.print(" mbar; ");
  Serial.print(percBuff); //affichage du pourcentage de la pression mesurée en fonction de la plage de mesure
  Serial.println(" % ");
  lcd.setCursor(0, 1);//affichage de la pression sur le LCD 
  lcd.print("Pressure : ");
  lcd.print(pBuff);
  lcd.print(" mbar");
  delay(10);
}

void PWM_Blower() { // Cette fonction va permettre de générer le signal PPM qui va contrôler le blower, cette génération est sous la forme d'un timer pour créer un signal PWM
  pinMode(PIN_ESC_BLOWER, OUTPUT);
  hardwareTimer1 = new HardwareTimer(TIM4); //Sélectionne le timer 4 pour la pin D10
  hardwareTimer1->setOverflow(ESC_PPM_PERIOD, MICROSEC_FORMAT); //Définit la période/fréquence de la PWM
  hardwareTimer1->refresh(); //réninitialise le timer
  hardwareTimer1->setMode(TIM_CHANNEL_ESC_BLOWER, TIMER_OUTPUT_COMPARE_PWM1, PIN_ESC_BLOWER); //Permet de mettre le mode PWM sur le timer (Autres modes : Input Capture/Ouput Capture/One-pulse
  // Set PPM width to 1ms
  hardwareTimer1->setCaptureCompare(TIM_CHANNEL_ESC_BLOWER, BlowerSpeed2MicroSeconds(500), MICROSEC_COMPARE_FORMAT); //Définit le rapport cyclique de la PWM
  hardwareTimer1->attachInterrupt(TIM_CHANNEL_ESC_BLOWER, expiration); //Active la fonction à chaque interruption
  hardwareTimer1->resume(); //Lance le timer
}

void Airflow_Timer() { // Cette fonction va permettre de générer le timer pour la fonction du débitmètre
  hardwareTimer2 = new HardwareTimer(TIM1); //Sélectionne le timer 1 
  hardwareTimer2->setOverflow(AIRFLOW_PERIOD, MICROSEC_FORMAT); //Définit la période/fréquence du timer
  hardwareTimer2->refresh(); //réninitialise le timer
  hardwareTimer2->setMode(TIM_CHANNEL_AIRFLOW, TIMER_OUTPUT_COMPARE); //Permet de mettre le mode OC sur le timer (Autres modes : Input Capture/PWM/One-pulse
  hardwareTimer2->setCaptureCompare(TIM_CHANNEL_AIRFLOW, 0 , PERCENT_COMPARE_FORMAT); //Définit le début du compteur
  hardwareTimer2->attachInterrupt(TIM_CHANNEL_AIRFLOW, airFlow); //Active la fonction à chaque interruption
  hardwareTimer2->resume(); //Lance le timer
}

void Pressure_Timer() { // Cette fonction va permettre de générer le du timer pour la fonction du capteur de pression
  hardwareTimer3 = new HardwareTimer(TIM2); //Sélectionne le timer 2
  hardwareTimer3->setOverflow(PRESSURE_PERIOD, MICROSEC_FORMAT); //Définit la période/fréquence du timer
  hardwareTimer3->refresh(); //réninitialise le timer
  hardwareTimer3->setMode(TIM_CHANNEL_PRESSURE, TIMER_OUTPUT_COMPARE); //Permet de mettre le mode OC sur le timer (Autres modes : Input Capture/PWM/One-pulse
  hardwareTimer3->setCaptureCompare(TIM_CHANNEL_PRESSURE, 0 , PERCENT_COMPARE_FORMAT); //Définit le début du compteur
  hardwareTimer3->attachInterrupt(TIM_CHANNEL_PRESSURE, Pressure); //Active la fonction à chaque interruption
  hardwareTimer3->resume(); //Lance le timer
}

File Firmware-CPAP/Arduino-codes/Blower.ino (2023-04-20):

#define ESC_PPM_PERIOD 20000 // 50Hz
#define MIN_BLOWER_SPEED 300u
#define MAX_BLOWER_SPEED 1800u
#define DEFAULT_BLOWER_SPEED 900u
#define PIN_ESC_BLOWER  PB6  // D10 / TIM4_CH1
#define TIM_CHANNEL_ESC_BLOWER 1 //Channel 1 de la pin D10
#define BlowerSpeed2MicroSeconds(value) map(value, 0, 1800, 1000, 1950) //Intervalle [1ms à 1,95 ms] sur la variation de vitesse du blower, on élargit cette intervalle pour avoir une plus grande plage de commande du Blower
#include "HardwareTimer.h"
#include <LiquidCrystal.h>

HardwareTimer* hardwareTimer1;  // Timer Blower command

LiquidCrystal lcd(PA10, PB4, PA9, PC7, PA7, PA6);

////Variables Blower////
static int speedBlower = DEFAULT_BLOWER_SPEED;

///////Anti-rebond/////////
int reading, reading2 = 0;
int buttonState = 1;            // état courant du bouton 
int lastButtonState = 0;  // état précédent du bouton
int buttonState2 = 1;            
int lastButtonState2 = 0;  
unsigned long lastDebounceTime = 50;  // le temps précédent du changement d'état du bouton
unsigned long debounceDelay = 0;    // Delai de l'anti rebond, l'augmenter si il y a encore des rebonds sur le bouton
unsigned long lastDebounceTime2 = 50;  
unsigned long debounceDelay2 = 0;   
////////////////////////

void setup() {
  Serial.begin(115200);
  lcd.begin(20, 4);
  pinMode(PA8, INPUT_PULLUP); //D7
  pinMode(PB5, INPUT_PULLUP); //D4
  PWM_Blower();
}

void loop() {

}

void PWM_Blower() { // Cette fonction va permettre de générer le signal PPM qui va contrôler le blower, cette génération est sous la forme d'un timer pour créer un signal PWM
  pinMode(PIN_ESC_BLOWER, OUTPUT);
  hardwareTimer1 = new HardwareTimer(TIM4); //Sélectionne le timer 4 pour la pin D10
  hardwareTimer1->setOverflow(ESC_PPM_PERIOD, MICROSEC_FORMAT); //Définit la période/fréquence de la PWM
  hardwareTimer1->refresh(); //réninitialise le timer
  hardwareTimer1->setMode(TIM_CHANNEL_ESC_BLOWER, TIMER_OUTPUT_COMPARE_PWM1, PIN_ESC_BLOWER); //Permet de mettre le mode PWM sur le timer (Autres modes : Input Capture/Ouput Capture/One-pulse
  // Set PPM width to 1ms
  hardwareTimer1->setCaptureCompare(TIM_CHANNEL_ESC_BLOWER, BlowerSpeed2MicroSeconds(DEFAULT_BLOWER_SPEED), MICROSEC_COMPARE_FORMAT); //Définit le rapport cyclique de la PWM
  hardwareTimer1->attachInterrupt(TIM_CHANNEL_ESC_BLOWER, expiration); //Active la fonction à chaque interruption
  hardwareTimer1->resume(); //Lance le timer
}

void expiration() {
  reading = digitalRead(PA8);
  if (reading != lastButtonState) {
    // réinitialisation de l'anti-rebond
    lastDebounceTime = millis();
  }
  if ((millis() - lastDebounceTime) > debounceDelay) {
    // Condition du changement d'état du bouton
    if (reading != buttonState) {
      buttonState = reading;
      // Instruction exécutée si le bouton est LOW
      if (buttonState == 0) {
        speedBlower -= 10;
      }
    }
  }
  lastButtonState = reading;

  reading2 = digitalRead(PB5);
  if (reading2 != lastButtonState2) {
    // réinitialisation de l'anti-rebond
    lastDebounceTime2 = millis();
  }
  if ((millis() - lastDebounceTime2) > debounceDelay2) {
    // Condition du changement d'état du bouton
    if (reading2 != buttonState2) {
      buttonState2 = reading2;
      // Instruction exécutée si le bouton est LOW
      if (buttonState2 == 0) {
        speedBlower += 10;
      }
    }
  }
  lastButtonState2 = reading2;

  if (speedBlower <= 100)  speedBlower = 100; //Limitation de la valeur min
  if (speedBlower >= 1800)  speedBlower = 1800; //Limitation de la valeur max
  lcd.setCursor(0, 0);
  lcd.print(speedBlower);
  hardwareTimer1->setCaptureCompare(TIM_CHANNEL_ESC_BLOWER, BlowerSpeed2MicroSeconds(speedBlower), MICROSEC_COMPARE_FORMAT); //Changement du rapport cyclique
}

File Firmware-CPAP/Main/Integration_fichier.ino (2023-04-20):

#define AIRFLOW_PERIOD 200000 // 5Hz
#define PRESSURE_PERIOD 1000000 //1Hz

#include <LiquidCrystal.h>

#include "airflowSensor.h"
#include "pressureSensor.h"
#include "blower.h"
#include "IHM.h"

LiquidCrystal lcd(PA10, PB4, PA9, PC7, PA7, PA6); //Attribution de l'Afficheur

int configuration = 0;
int vitesse = DEFAULT_BLOWER_SPEED;
int Speed = 0;

void setup() {
  Serial.begin(115200);
  lcd.begin(20, 4); //Initialisation de l'afficheur LCD
  Airflow_init();
  Pressure_init();
  Blower_init();
  Airflow_Timer(AIRFLOW_PERIOD);
  Pressure_Timer(PRESSURE_PERIOD);
  Speed = map(vitesse, 300, 1800, 0, 100);
}

void loop() {
lcd.setCursor(0,0);
lcd.print("Debit : ");
lcd.print(getAirflow());
lcd.print(" SLPM");
lcd.setCursor(0,1);
lcd.print("Pression : ");
lcd.print(getPres());
lcd.print(" mbar");
lcd.setCursor(0,2);
lcd.print("Vitesse : ");
lcd.print(Speed);
lcd.print(" %");
configuration = debounceConfig(PC13,50,configuration,1);
if(configuration == 1){
  arret();
  vitesse = debounceMore(PB5,50,vitesse,15,1800); 
  vitesse = debounceLess(PA8,50,vitesse,15,300);
  configuration = debounceConfig(PC13,50,configuration,2);
  Speed = map(vitesse, 300, 1800, 0, 100);
  Serial.println(vitesse);
 }
else if(configuration == 2){
  setVitesse(vitesse);
  configuration = 0;
 }
}
